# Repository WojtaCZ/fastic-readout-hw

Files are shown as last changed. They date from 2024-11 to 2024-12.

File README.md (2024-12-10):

# FastIC+ readout 

This repository contains the project files and manufacturing outputs for the FastIC+ readout. The files for the [userboard](https://github.com/WojtaCZ/fastic-userboard-hw) are also available to simplify development of sensor boards compatible with the readout.

<div align="center">
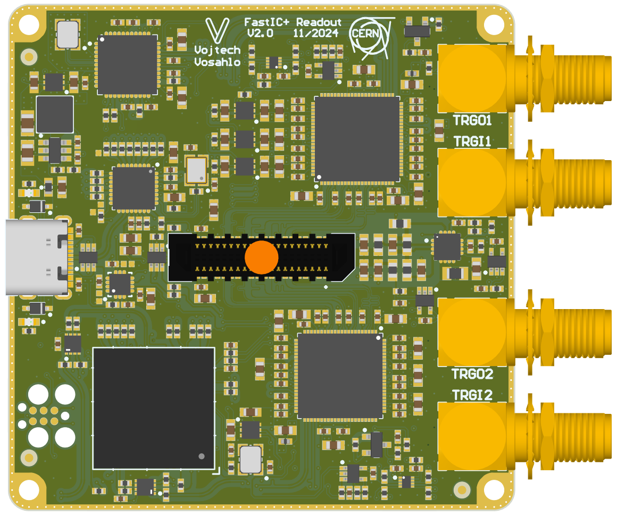
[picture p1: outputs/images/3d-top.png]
  
  
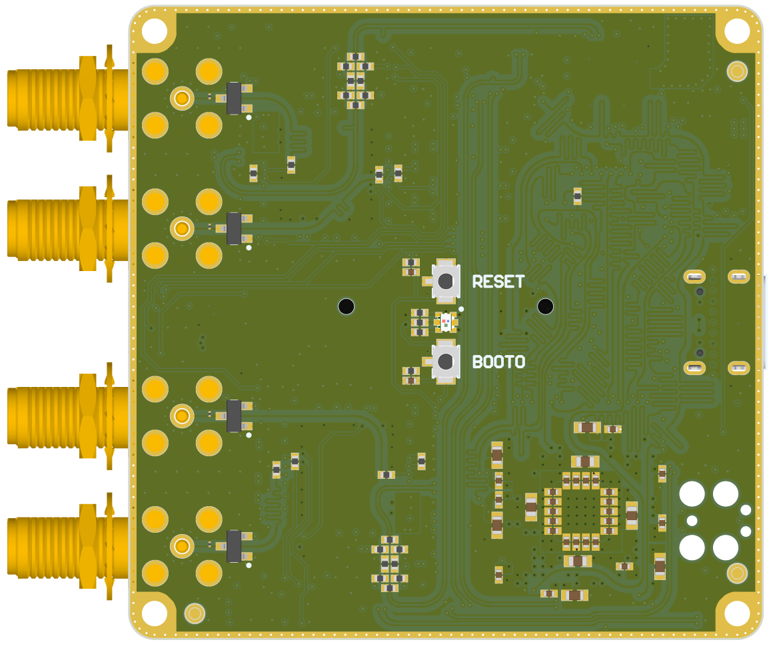
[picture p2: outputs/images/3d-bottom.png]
   
</div>

## Output files
Schematic, BOM and 3D renders are available in the outputs folder aswell as the gerbers and pick and place files needed for assembly. Gerbers and P&P files for both a single board and a 2x2 panel are provided.

## Flashing the firmware

Before the first startup, the onboard [Tag-Connect 6 pin SWD connector](https://www.tag-connect.com/product/tc2030-ctx-stdc14-for-use-with-stm32-processors-with-stlink-v3) shall be used with a compatible programmer like [STLINK-V3](https://www.st.com/en/development-tools/stlink-v3set.html) to flash the device with the bootloader provided.

After the bootloader has been flashed, the boot address option bytes shall be programmed to the following values:
**BOOT_CM7_ADD0** = 0x08020000
**BOOT_CM7_ADD1** = 0x08000000

After this procedure is complete, connect the device

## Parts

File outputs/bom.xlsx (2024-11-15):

Name | Voltage | Case | Description | Designator | Quantity | Manufacturer 1 | Manufacturer Part Number 1 | Manufacturer Lifecycle 1 | Supplier 1 | Supplier Part Number 1 | Supplier Order Qty 1 | Supplier Stock 1 | Supplier Unit Price 1 | Supplier Subtotal 1 | Fitted
0 |  | 0402 | Resistor | R86, R87, R88, R107 | 4 | Yageo | RC0402JR-070RL | Volume Production | Digikey | 311-0.0JRDKR-ND | 160 | 13484543 | 0.0019 | 0.30359
1M |  | 0402 | Resistor - 1% | R106 | 1 | Yageo | RC0402FR-071ML | Volume Production | Digikey | 311-1.00MLRCT-ND | 40 | 1565307 | 0.00854 | 0.34154
1.5A |  | 0603 | Fuse | F1 | 1 | Bourns | SF-0603F150-2 | Volume Production | Digikey | SF-0603F150-2CT-ND | 40 | 21164 | 0.43926 | 17.57
3.3uH |  |  | Inductor With Core | L2 | 1 | Coilcraft | XAL4030-332MEC | Volume Production | Mouser | 994-XAL4030-332MEC | 40 | 59290 | 2.55 | 102.08
4k7 |  | 0402 | Resistor - 1% | R34_FASTIC1, R34_FASTIC2, R35_FASTIC1, R35_FASTIC2, R39_FASTIC1, R39_FASTIC2, R40_FASTIC1, R40_FASTIC2, R42_FASTIC1, R42_FASTIC2, R43_FASTIC1, R43_FASTIC2, R51, R52 | 14 | Yageo | RC0402FR-074K7L | Volume Production | Digikey | 311-4.7KLRCT-ND | 560 | 3599165 | 0.00387 | 2.17
8k06 |  | 0402 | Resistor - 1% | R105 | 1 | Yageo | RC0402FR-078K06L | Volume Production | Digikey | 311-8.06KLRCT-ND | 40 | 326268 | 0.00854 | 0.34154
10k |  | 0402 | Resistor - 0.1% | R38, R41_FASTIC1, R41_FASTIC2 | 3 | Yageo | RT0402BRD0710KL | Volume Production | Digikey | YAG1346CT-ND | 120 | 30079 | 0.08131 | 9.76
10k |  | 0402 | Resistor - 1% | R27_FASTIC1, R27_FASTIC2, R28_FASTIC1, R28_FASTIC2, R29_FASTIC1, R29_FASTIC2, R47, R48, R49, R50, R60, R79, R80, R85, R100, R108 | 16 | Yageo | RC0402FR-0710KL | Volume Production | Digikey | 311-10.0KLRDKR-ND | 640 | 6813886 | 0.00387 | 2.48
12k |  | 0402 | Resistor - 1% | R56, R61 | 2 | Yageo | RC0402FR-0712KL | Volume Production | Digikey | 311-12.0KLRDKR-ND | 100 | 176722 | 0.00484 | 0.48385
12k |  | 0603 | Resistor - 1% | R62 | 1 | Yageo | RC0603FR-0712KL | Volume Production | Mouser | 603-RC0603FR-0712KL | 40 | 161414 | 0.01044 | 0.41744
15k |  | 0402 | Resistor - 1% | R59 | 1 | Yageo | RC0402FR-0715KL | Volume Production | Digikey | 311-15.0KLRDKR-ND | 40 | 1511973 | 0.00854 | 0.34154
15uH |  | 0805 | Inductor | L3 | 1 | TDK | MLZ2012M150WT000 | Volume Production | Digikey | 445-6397-1-ND | 40 | 94015 | 0.06451 | 2.58
20 |  | 0402 | Resistor - 1% | R5, R6, R15, R16 | 4 | Yageo | RC0402FR-0720RL | Volume Production | Digikey | 311-20LRDKR-ND | 160 | 1408462 | 0.00389 | 0.62236
20 |  | 0603 | Resistor - 0.1% | R55 | 1 | Yageo | RT0603BRD0720RL | Volume Production | Digikey | 13-RT0603BRD0720RLCT-ND | 50 | 19030 | 0.08026 | 4.01
22 |  | 0402 | Resistor - 1% | R7, R8, R10, R17, R20, R24, R25, R26, R30_FASTIC1, R30_FASTIC2, R68, R69, R70, R71, R72, R73, R74, R75, R76, R77, R78, R81, R83, R84, R89, R90, R92, R94, R96, R97, R98, R99, R102, R103, R104 | 35 | Yageo | RC0402FR-0722RL | Volume Production | Digikey | 311-22.0LRCT-ND | 1400 | 1054177 | 0.0029 | 4.06
24MHz |  |  | Crystal 4 pins 1=XTAL Control 2=GND3=XTAL 4=GND | Q3 | 1 | Kyocera AVX | CX3225SB24000H0PSTC1 | Volume Production | Digikey | 478-CX3225SB24000H0PSTC1CT-ND | 40 | 16988 | 0.54836 | 21.93
48MHz |  |  | Crystal 4 pins 1=XTAL Control 2=GND3=XTAL 4=GND | Q1, Q2 | 2 | Kyocera AVX | CX3225SB48000D0FPJC1 | Volume Production | Digikey | 478-CX3225SB48000D0FPJC1CT-ND | 80 | 11492 | 0.84076 | 67.26
50 |  | 0402 | Resistor - 1% | R3, R4, R9, R13, R14, R23 | 6 | Yageo | RT0402BRE0750RL | Volume Production | Digikey | 13-RT0402BRE0750RLCT-ND | 240 | 12137 | 0.08225 | 19.74
100 |  | 0603 | Resistor - 1% | R54 | 1 | Yageo | RC0603FR-07100RL | Volume Production | Digikey | 311-100HRCT-ND | 40 | 1340836 | 0.01138 | 0.45539
200k |  | 0402 | Resistor - 1% | R36_FASTIC1, R36_FASTIC2 | 2 | Yageo | RC0402FR-07200KL | Volume Production | Digikey | 311-200KLRCT-ND | 100 | 761767 | 0.00389 | 0.38898
220 |  | 0402 | Resistor - 1% | R1, R2, R11, R12, R18, R19, R21, R22, R31_FASTIC1, R31_FASTIC2, R82, R123, R124, R126 | 14 | Yageo | RC0402FR-07220RL | Volume Production | Digikey | 311-220LRDKR-ND | 560 | 521190 | 0.0029 | 1.63
220R@100MHz |  | 0402 |  | L1_FASTIC1, L1_FASTIC2 | 2 | Murata | BLM15HB221SN1D | Volume Production | Digikey | 490-4001-1-ND | 80 | 568863 | 0.03415 | 2.73
AD8541AKSZ-R2 |  | SOT353 | Operational Amplifier | IC3_FASTIC1, IC3_FASTIC2, IC10, IC30 | 4 | Analog Devices | AD8541AKSZ-REEL7 | Volume Production | Digikey | 505-AD8541AKSZ-REEL7CT-ND | 160 | 2723 | 0.8399 | 134.38
AP62201WU-7 |  | SOT23-6 | 4.2V TO 18V INPUT, 2A LOW IQ SYNCHRONOUS BUCK CONVERTER | IC21 | 1 | Diodes | AP62201WU-7 | Volume Production | Digikey | 31-AP62201WU-7CT-ND | 40 | 70192 | 0.33926 | 13.57
DS90LVRA2-Q1 |  |  |  | IC1_FASTIC1, IC1_FASTIC2 | 2 | Texas Instruments | D9LVRA2DEMRQ1 | Unknown | Digikey | 296-D9LVRA2DEMRQ1CT-ND | 80 | 2870 | 2.05 | 163.88
ERM8-020-X-X-DV |  |  |  | J3 | 1 | Samtec | ERM8-020-09.0-L-DV-K-TR | Volume Production | Digikey | SAM13142CT-ND | 40 | 4010 | 4.12 | 164.83
FastIC+ |  | QFN89 |  | IC18_FASTIC1, IC18_FASTIC2 | 2
FUSB302BMPX |  | QFN14 | Programmable USB Type-C Controller with PD (Default SNK) | IC14 | 1 | ON Semiconductor / Fairchild | FUSB302BMPX | Volume Production | Digikey | FUSB302BMPXCT-ND | 40 | 1 | 0.88573 | 35.43
Green |  | 0603 | LED Green 1C 2A | LD13, LD14 | 2 | Kingbright | KPH-1608CGCK | Volume Production | Rs | 8610080 | 80 | 250 | 0.11949 | 9.56
IRLML6402PBF |  | SOT23-3 | P-CHANNEL MOSFET WITH ZENER DIODE | T1_FASTIC1, T1_FASTIC2 | 2 | Infineon | IRLML6402TRPBF | Not Recommended for New Design | Digikey | IRLML6402PBFCT-ND | 100 | 108447 | 0.20009 | 20.01
LT3571 |  |  |  | IC11 | 1 | Analog Devices / Linear Technology | LT3571EUD#TRPBF | Volume Production | Digikey | LT3571EUD#TRPBFCT-ND | 40 | 2349 | 3.35 | 133.9
PCA9306DQER |  |  |  | IC2_FASTIC1, IC2_FASTIC2 | 2 | Texas Instruments | PCA9306DQER | Volume Production | Digikey | 296-27957-1-ND | 80 | 2437 | 0.41061 | 32.85
PESD1V2 |  |  |  | D2, D4, D7, D9 | 4 | Nexperia | PESD1V2Y1BSFYL | Unknown | Digikey | 1727-PESD1V2Y1BSFYLCT-ND | 160 | 27453 | 0.09487 | 15.18
Push Button |  |  | Push-Button Switch SPST | PB1, PB2 | 2 | Omron | B3U-1100P | Volume Production | Digikey | SW1021CT-ND | 80 | 52544 | 0.70205 | 56.16
Red/Green/Blue |  |  | Everlight Tricolor (Red/Green/Blue) Surface Mount LED | LD15 | 1 | Everlight | EAST1616RGBA8 | Volume Production | Digikey | 1080-EAST1616RGBA8CT-ND | 40 | 71176 | 0.30359 | 12.14
SI5340B-D-GM |  | QFN44 | Low-Jitter, 4-Output, Any-Frequency, Any-Output Clock Generator | IC9 | 1 | Skyworks Solutions | SI5340B-D-GM | Unknown | Digikey | SI5340B-D-GM-ND | 40 | 1377 | 13.12 | 524.88
SMA |  |  |  | J1, J2, J4, J5 | 4 | Amphenol Connex | 132203 | Volume Production | Digikey | ACX1234-ND | 160 | 1995 | 8.62 | 1378.55
STM32H753XIH6 |  |  | No Description Available | U1 | 1 | STMicroelectronics | STM32H753XIH6 | Volume Production | Digikey | 497-18567-ND | 40 | 2046 | 14.91 | 596.42
TC2030-MCP |  |  | TC2030-MCP and TC2030-MCP-NL Pad Contact | J6 | 1
TPS74612PQWDRVRQ1 |  |  |  | IC6, IC7, IC8 | 3 | Texas Instruments | TPS74612PQWDRVRQ1 | Volume Production | Digikey | 296-TPS74612PQWDRVRQ1CT-ND | 120 | 8699 | 0.63564 | 76.28
TPS74618PQWDRVRQ1 |  |  |  | IC4 | 1 | Texas Instruments | TPS74618PQWDRVRQ1 | Volume Production | Digikey | 296-TPS74618PQWDRVRQ1CT-ND | 40 | 5618 | 0.7863 | 31.45
TPS74633PQWDRVRQ1 |  |  |  | IC5 | 1 | Texas Instruments | TPS74633PQWDRVRQ1 | Volume Production | Digikey | 296-TPS74633PQWDRVRQ1CT-ND | 40 | 1190 | 0.7863 | 31.45
USB3320C-EZK-TR |  | QFN32 | Highly Integrated, Full Featured Hi-Speed USB 2.0 ULPI Transceiver | IC13 | 1 | Microchip | USB3320C-EZK-TR | Volume Production | Digikey | USB3320C-EZK-DKR-ND | 40 | 12766 | 1.71 | 68.31
USB 2.0 |  |  | 2x8 Pin + 1 Shield USB Type C Receptacle | J7 | 1 | Global Connector Technology | USB4105-GF-A | Unknown | Digikey | 2073-USB4105-GF-ACT-ND | 40 | 27005 | 0.67207 | 26.88
Use only in PCB |  |  | Fiducial Target | FTG3, FTG4, FTG5, FTG6 | 4
PESD5V0S1UA | 5V | SOD323 | Transient Voltage Suppressor Diode (Uni-Directional) | D10, D12 | 2 | Nexperia | PESD5V0S1UA,115 | Volume Production | Digikey | 1727-5801-1-ND | 100 | 6261 | 0.09487 | 9.49
4.7uF | 6.3V | 0603 | Non-polarised capacitor | C18, C19, C20, C21, C39, C46, C47_FASTIC1, C47_FASTIC2, C59_FASTIC1, C59_FASTIC2, C60_FASTIC1, C60_FASTIC2, C67_FASTIC1, C67_FASTIC2, C68_FASTIC1, C68_FASTIC2, C74_FASTIC1, C74_FASTIC2, C76, C79_FASTIC1, C79_FASTIC2, C82_FASTIC1, C82_FASTIC2, C85_FASTIC1, C85_FASTIC2 | 25 | Murata | GRM188R6YA475KE15D | Volume Production | Digikey | 490-7205-1-ND | 1000 | 100907 | 0.07119 | 71.19
D3V3F4U6S | 8kV | SOT363 | Integrated Quad Ultra-Low Capacitance ESD Protection | D5, D11 | 2 | Diodes | D3V3F4U6S-7 | Volume Production | Digikey | 31-D3V3F4U6S-7CT-ND | 100 | 69009 | 0.13946 | 13.95
2.2uF | 10V | 0603 | Non-polarised capacitor | C3, C4, C25, C26, C27, C28, C29, C30, C31, C32, C33, C34, C94, C96, C100, C102, C118, C120, C124, C126, C129, C133, C136 | 23 | Murata | GRM188R71A225KE15D | Volume Production | Digikey | 490-4520-6-ND | 1000 | 657122 | 0.03714 | 37.14
100nF | 16V | 0402 | Non-polarised capacitor | C1, C2, C8_FASTIC1, C8_FASTIC2, C9_FASTIC1, C9_FASTIC2, C10_FASTIC1, C10_FASTIC2, C11_FASTIC1, C11_FASTIC2, C12, C13, C14, C15, C16, C17, C35, C36, C37, C38, C40, C41, C42, C43, C44, C45, C48, C49, C51_FASTIC1, C51_FASTIC2, C52_FASTIC1, C52_FASTIC2, C53_FASTIC1, C53_FASTIC2, C54_FASTIC1, C54_FASTIC2, C55_FASTIC1, C55_FASTIC2, C56_FASTIC1, C56_FASTIC2, C57_FASTIC1, C57_FASTIC2, C58_FASTIC1, C58_FASTIC2, C61_FASTIC1, C61_FASTIC2, C62_FASTIC1, C62_FASTIC2, C63_FASTIC1, C63_FASTIC2, C64_FASTIC1, C64_FASTIC2, C65_FASTIC1, C65_FASTIC2, C66_FASTIC1, C66_FASTIC2, C70_FASTIC1, C70_FASTIC2, C71_FASTIC1, C71_FASTIC2, C72_FASTIC1, C72_FASTIC2, C73_FASTIC1, C73_FASTIC2, C75, C77_FASTIC1, C77_FASTIC2, C78_FASTIC1, C78_FASTIC2, C80_FASTIC1, C80_FASTIC2, C81_FASTIC1, C81_FASTIC2, C83_FASTIC1, C83_FASTIC2, C84_FASTIC1, C84_FASTIC2, C88, C90, C92, C93, C99, C101, C105, C106, C107, C108, C109, C110, C111, C112, C113, C114, C115, C116, C117, C119, C121, C122, C127, C128, C132, C137, C138, C139, C140, C141, C142, C145 | 109 | Murata | GRM155R71C104KA88D | Volume Production | Digikey | 490-3261-1-ND | 4360 | 12753171 | 0.00748 | 32.6
22uF | 25V | 0805 | Non-polarised capacitor | C97 | 1 | Murata | GRM21BR61A226ME51L | Volume Production | Digikey | 490-10511-1-ND | 50 | 411732 | 0.09203 | 4.6
10uF | 35V | 0805 | Non-polarised capacitor | C95 | 1 | Kyocera AVX | 0805YD106KAT2A | Volume Production | Digikey | 478-5165-6-ND | 50 | 64521 | 0.10626 | 5.31
330nF | 35V | 0402 | Non-polarised capacitor | C89 | 1 | Murata | GRM155R61A334KE15D | Volume Production | Digikey | 490-3263-1-ND | 50 | 980388 | 0.03814 | 1.91
1k | 50V | 0402 | Resistor - 0.1% | R53 | 1 | Yageo | RT0402DRE071KL | Volume Production | Digikey | 311-2252-1-ND | 40 | 30251 | 0.04838 | 1.94
3.3pF | 50V | 0402 | Non-polarised capacitor | C103, C104, C130, C131 | 4 | Murata | GRM1555C1H3R3CA01D | Volume Production | Digikey | 490-5938-1-ND | 160 | 1186839 | 0.01025 | 1.64
10nF | 50V | 0402 | Non-polarised capacitor | C22_FASTIC1, C22_FASTIC2, C23_FASTIC1, C23_FASTIC2, C69_FASTIC1, C69_FASTIC2, C147_FASTIC1, C147_FASTIC2, C148_FASTIC1, C148_FASTIC2 | 10 | KEMET | C0402C103K4RACTU | Volume Production | Digikey | 399-C0402C103K4RACTUCT-ND | 500 | 7965 | 0.0081 | 4.05
20k | 50V | 0402 | Resistor - 0.1% | R44_FASTIC1, R44_FASTIC2, R63 | 3 | Bourns | CR0402-FX-2002GLF | Volume Production | Digikey | CR0402-FX-2002GLFCT-ND | 120 | 168106 | 0.00446 | 0.53508
31k6 | 50V | 0402 | Resistor - 0.1% | R37 | 1 | Yageo | RT0402BRD0731K6L | Volume Production | Digikey | YAG1410CT-ND | 50 | 10906 | 0.09203 | 4.6
100 | 50V | 0402 | Resistor - 1% | R32_FASTIC1, R32_FASTIC2, R33_FASTIC1, R33_FASTIC2, R101, R125, R127, R128, R129, R130 | 10 | Yageo | RC0402FR-07100RL | Volume Production | Digikey | 311-100LRDKR-ND | 400 | 2996649 | 0.00484 | 1.94
100pF | 50V | 0402 | Non-polarised capacitor | C24, C146 | 2 | Murata | GRM1555C1H101JA01D | Volume Production | Digikey | 490-5922-1-ND | 80 | 1750082 | 0.01556 | 1.24
220pF | 50V | 0402 | Non-polarised capacitor | C134, C135 | 2 | Murata | GRM1555C1H221JA01D | Volume Production | Digikey | 490-1293-1-ND | 80 | 352817 | 0.02505 | 2
470pF | 50V | 0402 | Non-polarised capacitor | C7_FASTIC1, C7_FASTIC2 | 2 | Murata | GRM1555C1H471JA01D | Volume Production | Digikey | 490-1297-1-ND | 80 | 325017 | 0.01954 | 1.56
BAV99 | 70V | SOT23-3 | Serial Diode | D1, D3, D6, D8 | 4 | Nexperia | BAV99,215 | Volume Production | Digikey | 1727-2914-1-ND | 160 | 882514 | 0.04032 | 6.45
1M | 100V | 0603 | Resistor - 0.1% | R57, R58 | 2 | KOA Speer | RS73F1JTTD1004B | Volume Production | Digikey | 2019-RS73F1JTTD1004BTR-ND | 5000 | 5000 | 0.09149 | 457.47
10nF | 100V | 0603 | Non-polarised capacitor | C86 | 1 | TDK | CGA3EAC0G2A103J080AC | Volume Production | Mouser | 810-CGA3EAC0G2A103JC | 40 | 63497 | 0.14326 | 5.73
100nF | 100V | 0603 | Non-polarised capacitor | C5, C6, C50 | 3 | TDK | CGA3E3X7S2A104K080AB | Volume Production | Mouser | 810-CGA3E3X7S2A104K | 120 | 293535 | 0.0389 | 4.67
220nF | 100V | 0603 | Non-polarised capacitor | C87 | 1 | Taiyo Yuden | HMK107C7224KAHTE | Volume Production | Digikey | 587-5012-1-ND | 50 | 96438 | 0.09658 | 4.83

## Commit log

2024-05-14 Initial push
    [BOM_Digikey.xlsx, BOM_Other.xlsx, clock.SchDoc, fastic.SchDoc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]
2024-05-14 Changed footprint of C39 and C49 to 0402
    [BOM.xlsx, BOM_Other.xlsx, top.SchDoc]
2024-05-14 Changed footprint of C140 to 0805
    [hv.SchDoc]
2024-05-14 Changed LDOs to compact alternative
    [fastic.SchDoc, fastic_readout.PrjPcb, hv.SchDoc, mcu.SchDoc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]
2024-05-15 Exchanged some components for miniaturized versions
    [clock.SchDoc, fastic.SchDoc, fastic_readout.PrjPcb, mcu.SchDoc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]
2024-10-22 Schematic almost done
    [clock.SchDoc, fastic.SchDoc, fastic_readout.PrjPcb, fastic_readout.SCHLIB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]
2024-10-22 Schematic Finished
    [clock.SchDoc, fastic.SchDoc, hv.SchDoc, mcu.SchDoc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]
2024-10-24 Sorting components done
    [clock.SchDoc, fastic.SchDoc, fastic_readout.PcbLib, fastic_readout.PrjPcb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]
2024-10-24 Mosly got the layout figured
    [fastic.SchDoc, hv.SchDoc, mcu.SchDoc, top.SchDoc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]
2024-10-28 Almost all components placed
    [fastic.SchDoc, fastic_readout.PrjPcb, fastic_readout_PANEL.PcbDoc, hv.SchDoc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]
2024-10-29 Routing of main signals done
    [clock.SchDoc, fastic.SchDoc, fastic_readout_PANEL.PcbDoc, mcu.SchDoc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]
2024-10-30 Routing almost done
    [fastic.SchDoc, mcu.SchDoc, power.SchDoc, top.SchDoc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]
2024-10-31 Routing done
    [mcu.SchDoc, top.SchDoc, usb.SchDoc]
2024-11-01 All done. Just need to add texts
    [clock.SchDoc, fastic.SchDoc, fastic_readout_PANEL.PcbDoc, hv.SchDoc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]
2024-11-11 Ready for manufacturing
    [fastic.SchDoc, fastic_readout.PcbLib, fastic_readout.SCHLIB, fastic_readout_PANEL.PcbDoc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]
2024-11-11 Altered via sizes and added drill and layer stack tables
2024-11-13 Renamed files
    [BOM.xlsx, fastic-readout.PrjPcb, fastic_readout.PcbLib, fastic_readout.PrjPcb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]
2024-11-13 Added readme and images
    [power.SchDoc]
2024-11-13 Updated sheet parameters
    [clock.SchDoc, fastic-readout.PrjPcb, fastic.SchDoc, hv.SchDoc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]
2024-11-15 Added outputs
    [bom.xlsx, clock.SchDoc, fastic-readout.PrjPcb, fastic.SchDoc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]
2024-11-27 Tidied up reference designators in schematic
    [fastic-readout.PrjPcb, fastic.SchDoc, power.SchDoc, top.SchDoc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]
2024-11-27 Fixed C96 reference to C69
    [fastic-readout.PrjPcb, fastic.SchDoc]
2024-11-27 Fixed some schematic missalignments
    [fastic-readout.PrjPcb, power.SchDoc]
2024-11-28 Added panel files
    [fastic-readout.PrjPcb, fastic-readout_PANEL.PcbDoc, pick-and-place.csv]
2024-11-28 Added menton of the panel files in readme
    [pick-and-place.csv]
